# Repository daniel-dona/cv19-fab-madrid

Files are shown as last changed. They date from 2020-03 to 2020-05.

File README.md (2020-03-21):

# cv19-fab-madrid
Existen diferentes modelos que se están imprimiendo, además existen diferentes nomenclaturas para denominarlos. A partir de ahora usaré la nomenclatura contenida aquí: https://publishwith.me/QvTsJTppfb

##¿Qué imprimo?
Primero, antes de nada, imprime el modelo de calibración, deberás hacerlo siempre que cambies de extrusor u otro parámetro importante de tu impresora. Ajusta la expansión horizontal (y si quieres prueba también con el flow rate, pero es opcional). Si el modelo no entra, baja de -0.1 en -0.1 hasta que entre, si queda muy flojo, al revés.

Una vez calibrada, intenta imprimir el modelo acordado, actualmente (21/03/2020) es el HH-1 que puedes encontrar en la carpeta de modelos. También dentro puedes consultar un PDF con recomendaciones para imprimir la máscara.

¡A imprimir!

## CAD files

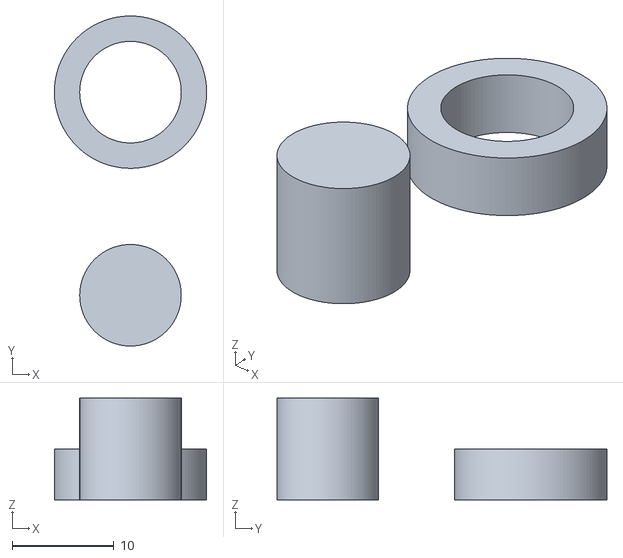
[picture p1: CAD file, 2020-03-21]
calibración/flow_calibrator.stl
15.0 x 32.5 x 10.0

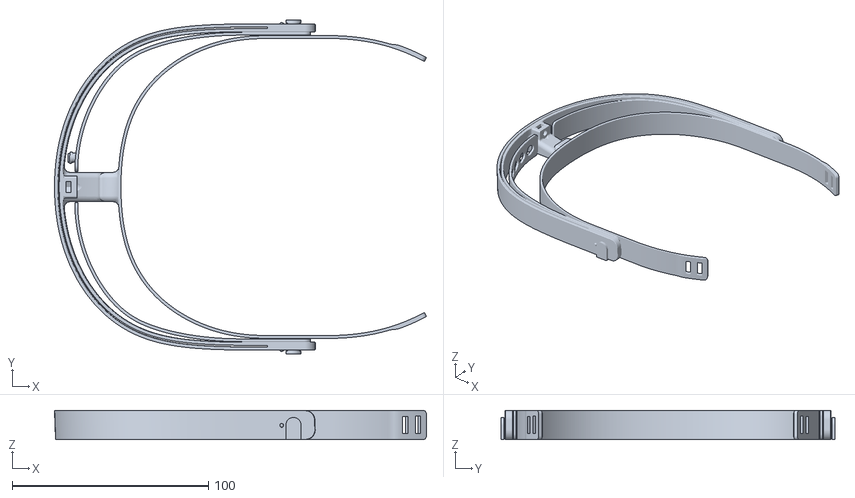
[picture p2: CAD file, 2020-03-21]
modelos/3.5.1/Visera_3.5.1_abierto.stl
189.7 x 170.4 x 15.0

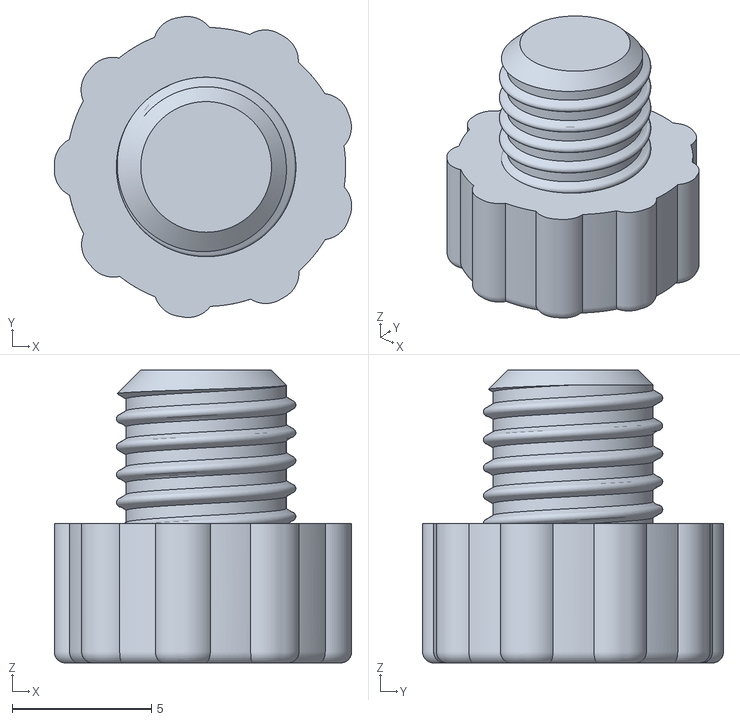
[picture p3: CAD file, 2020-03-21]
modelos/3.5.2/Tornillo_3.5.2.stl
10.7 x 10.8 x 10.5

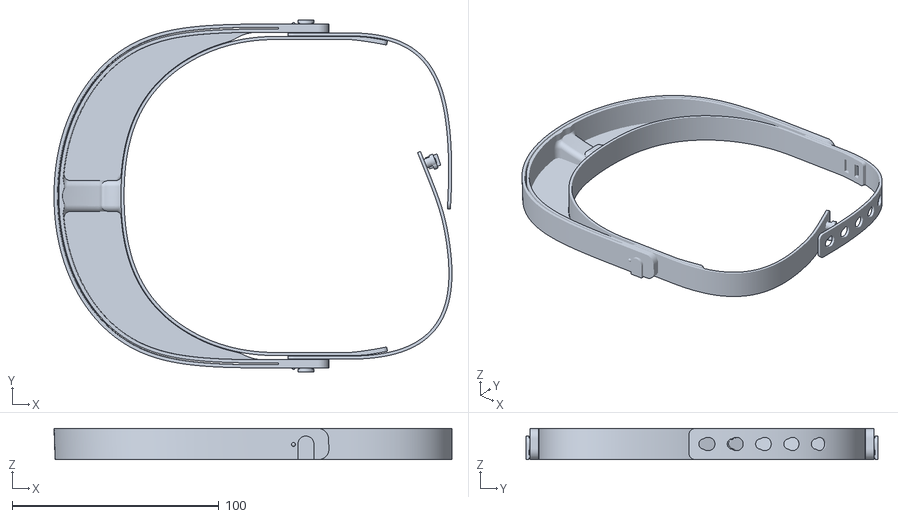
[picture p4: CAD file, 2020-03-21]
modelos/3.6b/Visera_3.6b_cerrada__mas_simple.stl
192.6 x 170.4 x 15.0

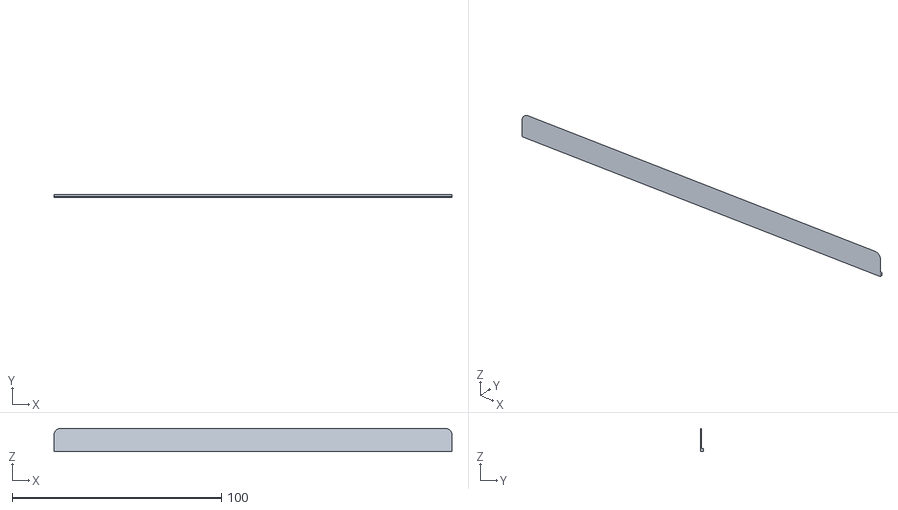
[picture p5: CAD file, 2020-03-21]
modelos/HH-1/Fijador_laminas_finas_300um.stl
190.0 x 1.20 x 11.0

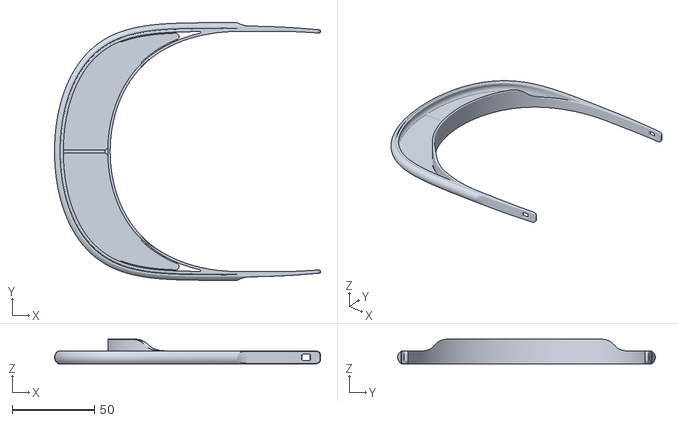
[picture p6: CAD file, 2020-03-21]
modelos/HH-3/Visera_Plana_con_cierre_y_ventilacion_0.3.stl
161.9 x 156.8 x 15.0

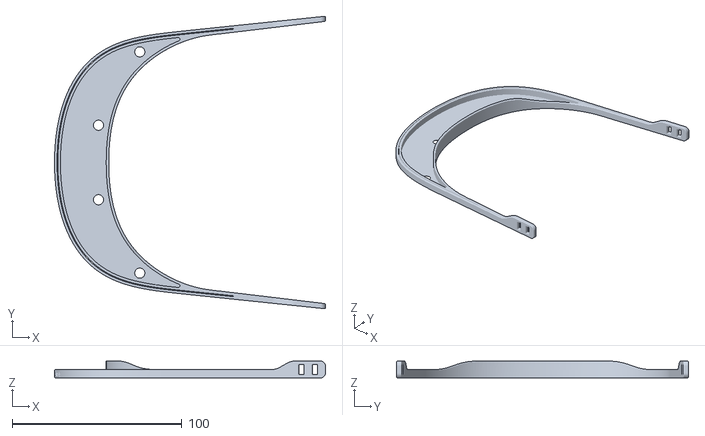
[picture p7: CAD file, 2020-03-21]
modelos/otros/Visera plana con ventilacion.stl
159.8 x 172.4 x 10.0

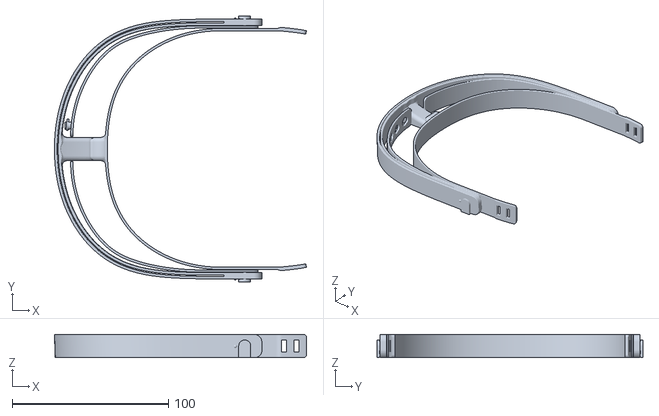
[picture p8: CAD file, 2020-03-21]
modelos/3.5.2/Visera_3.5.2.stl
161.5 x 170.4 x 15.0

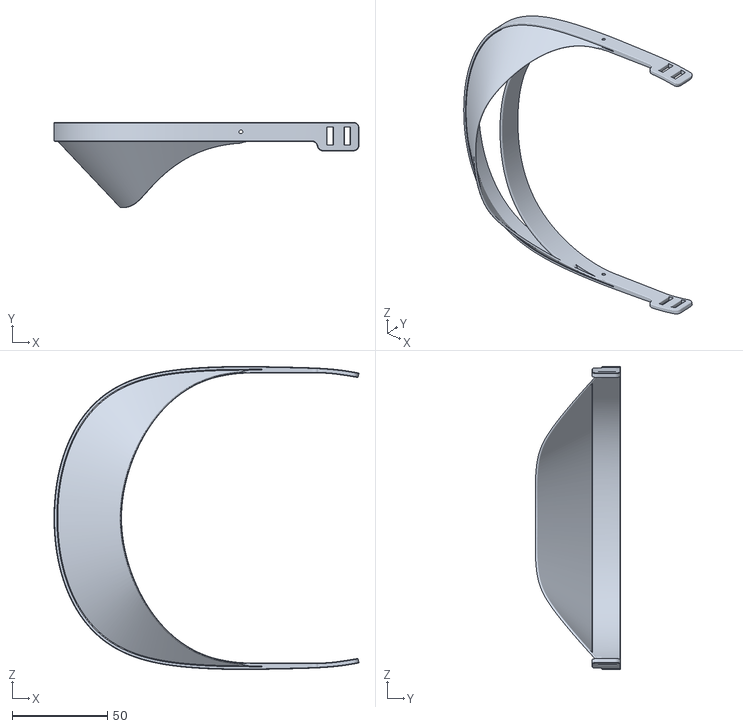
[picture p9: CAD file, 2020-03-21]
modelos/HH-1/Visera_Fija_Cerrada_v0.4_sin_logo.stl
159.9 x 44.8 x 159.0

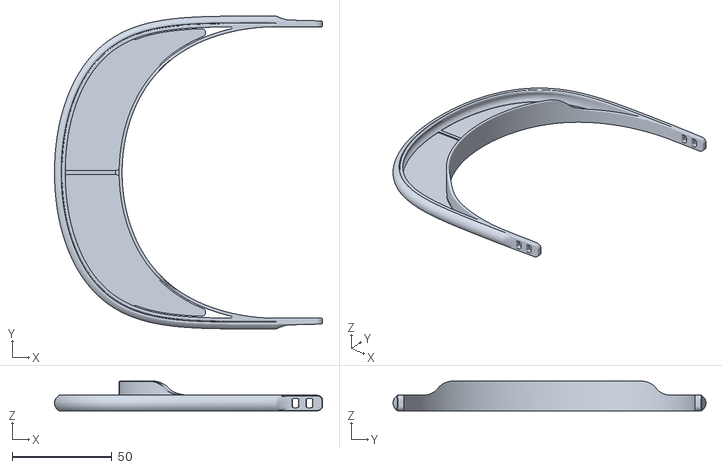
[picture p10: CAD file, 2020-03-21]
modelos/HH-3/Visera_Plana_con_cierre_y_ventilacion_0.4.stl
134.3 x 156.8 x 15.0

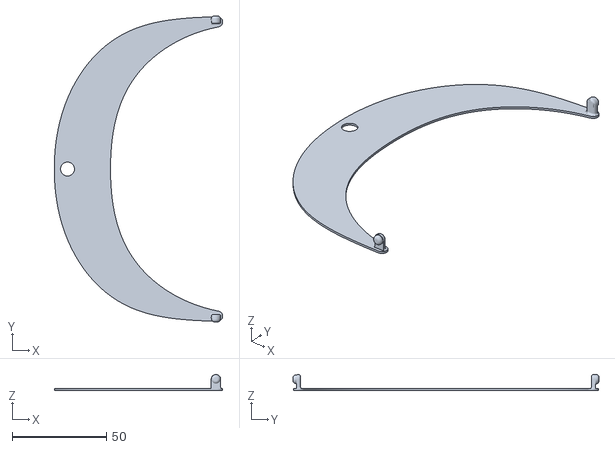
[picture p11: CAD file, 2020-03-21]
modelos/3.5.2/Tapa_3.5.2.stl
89.2 x 162.1 x 8.50

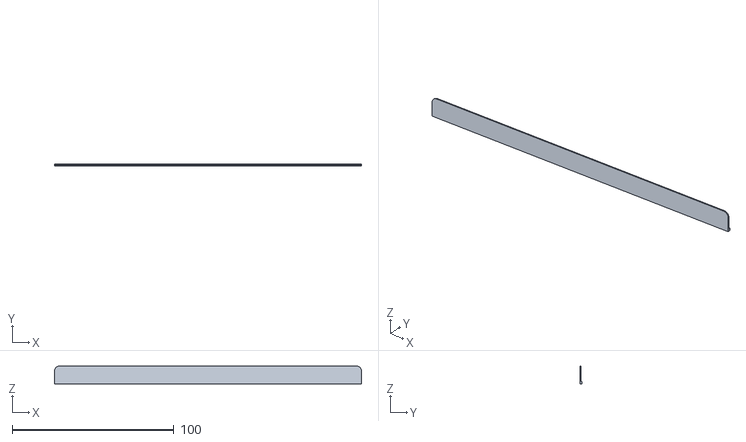
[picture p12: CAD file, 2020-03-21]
modelos/HH-1/Fijador_laminas_finas_600um.stl
190.0 x 1.50 x 11.0

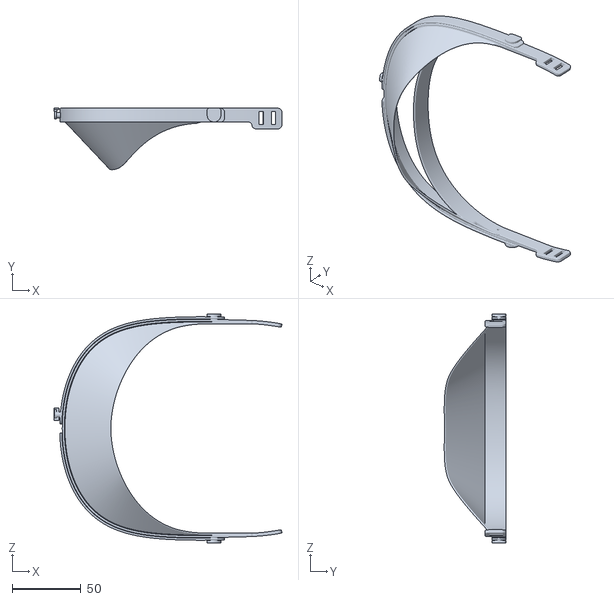
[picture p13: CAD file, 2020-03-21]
modelos/HH-1/Visera_Fija_Cerrada_v0.4_con_cinta_sin_logo.stl
165.9 x 44.8 x 166.3

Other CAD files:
modelos/HH-1/Visera_Fija_Cerrada_V0.4_STEP.step
modelos/HH-1/Visera_Fija_Cerrado_v0.4.stl
modelos/HH-1/Fijador_laminas_finas_500um.stl
modelos/HH-1/Fijador_laminas_finas_400um.stl

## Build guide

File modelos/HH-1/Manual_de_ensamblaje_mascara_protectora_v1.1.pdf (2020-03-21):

# Manual de impresión y ensamblaje mascara protectora

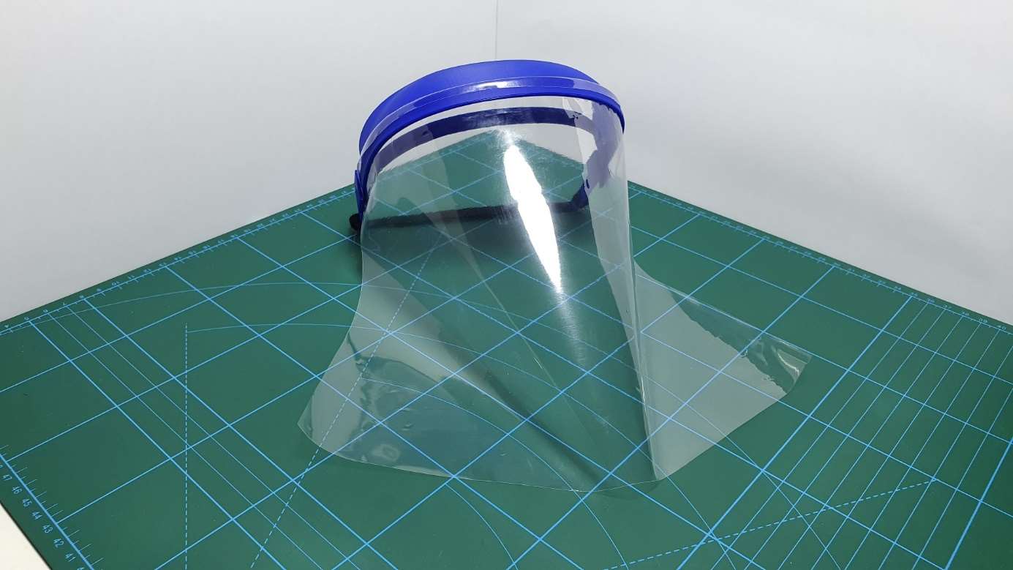
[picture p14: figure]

Página: 2/16

Página: 3/16

# Datos del Documento

Autor: | @YKA3D
Revisor: | @kermithenson
Fecha de publicación: | 18/03/2020
Observaciones:
Para comenzar a fabricar es necesario que la máquina esté correctamente calibrada. Una vez calibrada, se deberá llevar a cabo una prueba de tolerancia.

Test: https://www.thingiverse.com/thing:1662342

# Hoja de Cambios

Fecha | Versión | Autor | Cambios
18 de marzo de 2020 | v.0.1 | @YKA3D | Creación del documento
18 de marzo de 2020 | V.0.2 | @YKA3D | modificación fijación trasera
18 de marzo de 2020 | V.0.3 | @kermithenson | Modificación protocolos
19 de marzo de 2020 | V.0.4 | @YKA3D | Añadir manual modelo simple
19 de marzo de 2020 | V.1.0 | @YKA3D | Documento final
19 de marzo de 2020 | V.1.1 | @YKA3D | Modificaciones varias

# Versión STL

Fecha | Versión | Autor | Cambios
18 de marzo de 2020 | v.3.5 | @Hanochh | Creación STL mascara
18 de marzo de 2020 | V.0.1 | @3DYKA | Creación STL clip

Página: 4/16

# Índice

Introducción | 5
Enlace de compras | 6
Parámetros de impresión | 6
Ensamblaje de la máscara | 8

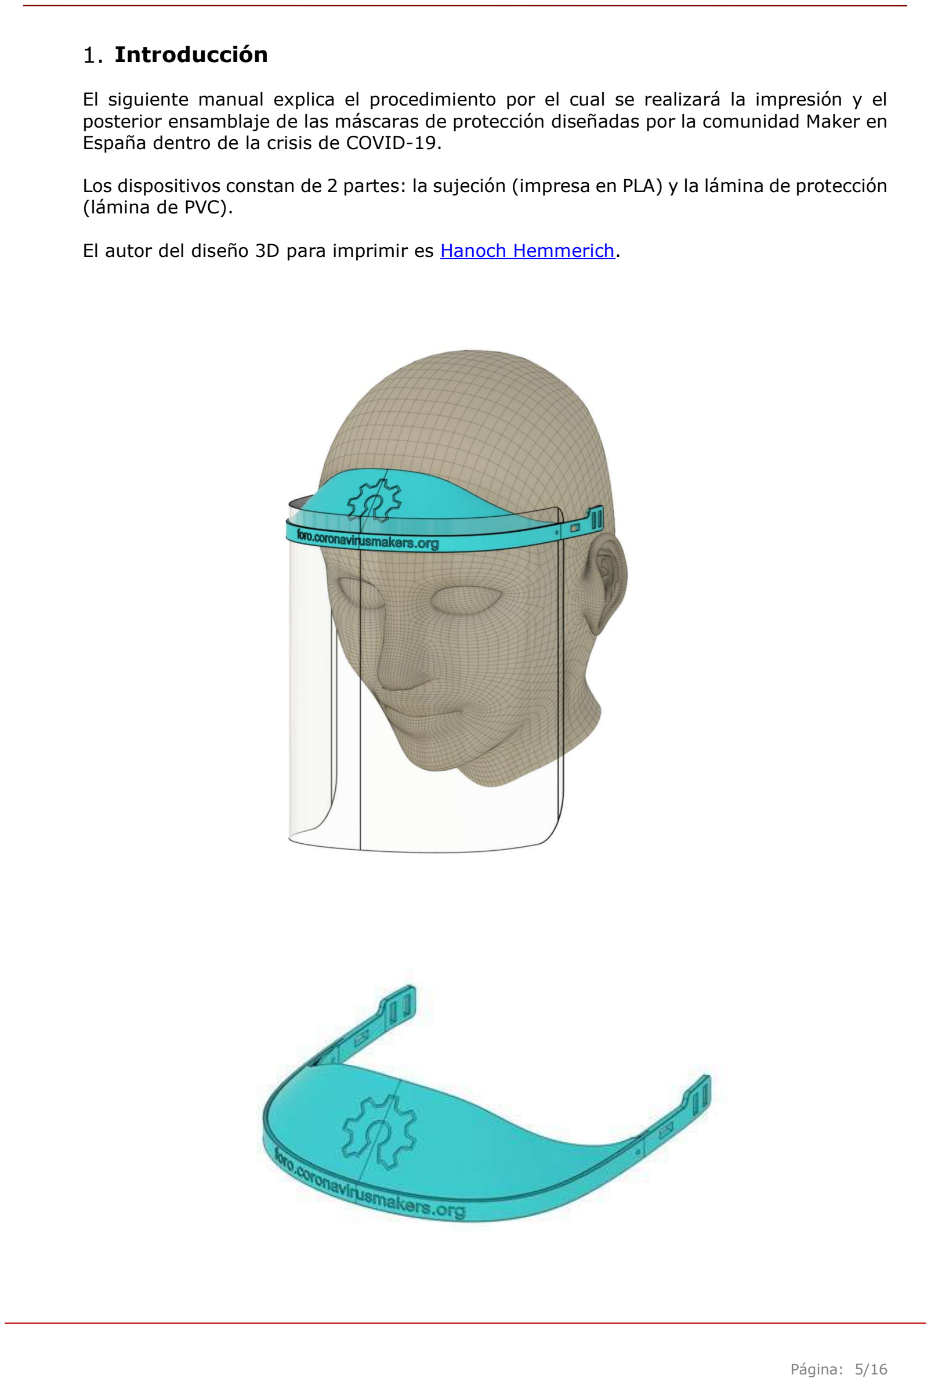
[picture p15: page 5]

Página: 5/16

### Introducción

El siguiente manual explica el procedimiento por el cual se realizará la impresión y el posterior ensamblaje de las máscaras de protección diseñadas por la comunidad Maker en España dentro de la crisis de COVID-19.

Los dispositivos constan de 2 partes: la sujeción (impresa en PLA) y la lámina de protección (lámina de PVC).

El autor del diseño 3D para imprimir es Hanoch Hemmerich.

Página: 6/16

### Enlace de compras

Los siguientes enlaces solo son una referencia del material utilizado para la elaboración de las pantallas protectoras.

- Láminas de encuadernar
o 180 micras
https://www.amazon.es/Fellowes-Cristal-Portadas-encuadernaci%C3%B3ntransparente/dp/B002BARBEK/ref=sr_1_1?__mk_es_ES=%C3%85M%C3%85%C5%BD%C3%95%C3%91&dchild=1&keywords=Fellowes+Portadas+para+encuadernar+de+PVC+transparente+180&qid=1584614023&s=office&sr=1-1
o 240 micras
https://www.amazon.es/gp/product/B000YC1UWG/ref=ppx_yo_dt_b_asin_title_o00_s00?ie=UTF8&psc=1
- Velcro para sujeción trasera https://www.amazon.es/gp/product/B07X2VMHJ5/ref=ppx_yo_dt_b_asin_image_o00_s00?ie=UTF8&psc=1
- Goma elástica
https://www.amazon.es/Banda-el%C3%A1stica-personalizada-Artesan%C3%ADametros/dp/B0749M5CBF/ref=sr_1_16?__mk_es_ES=%C3%85M%C3%85%C5%BD%C3%95%C3%91&crid=2QMWDSOIWQT2U&dchild=1&keywords=bobina+goma+elastica&qid=1584614347&refinements=p_85%3A831314031&rnid=831276031&rps=1&sprefix=bobina+goma+el%2Caps%2C151&sr=8-16

### Parámetros de impresión

El archivo para su impresión se puede descargar desde el siguiente enlace:

### https://www.thingiverse.com/thing:4230817

Los parámetros de impresión utilizados para el modelo son los siguientes:

- Diámetro del Nozzle: 0.4mm
- Altura de capa: 0.28mm
- Relleno: 50%
- Tipo de relleno: Rejilla
- Capas superiores: 4
- Capas inferiores: 2
- Flujo: 80%
- Sin soportes
- Velocidad de impresión:
o Perímetros: 80mm/s
o Perímetros pequeños: 80mm/s o Perímetros externos: 80mms/s o Relleno: 80mms/s
o Relleno solido: 80mms/s
o Relleno solido superior: 80mm/s o Puentes: 80mm/s
o Relleno: 80mm/s
o Recorrido: 180mm/s

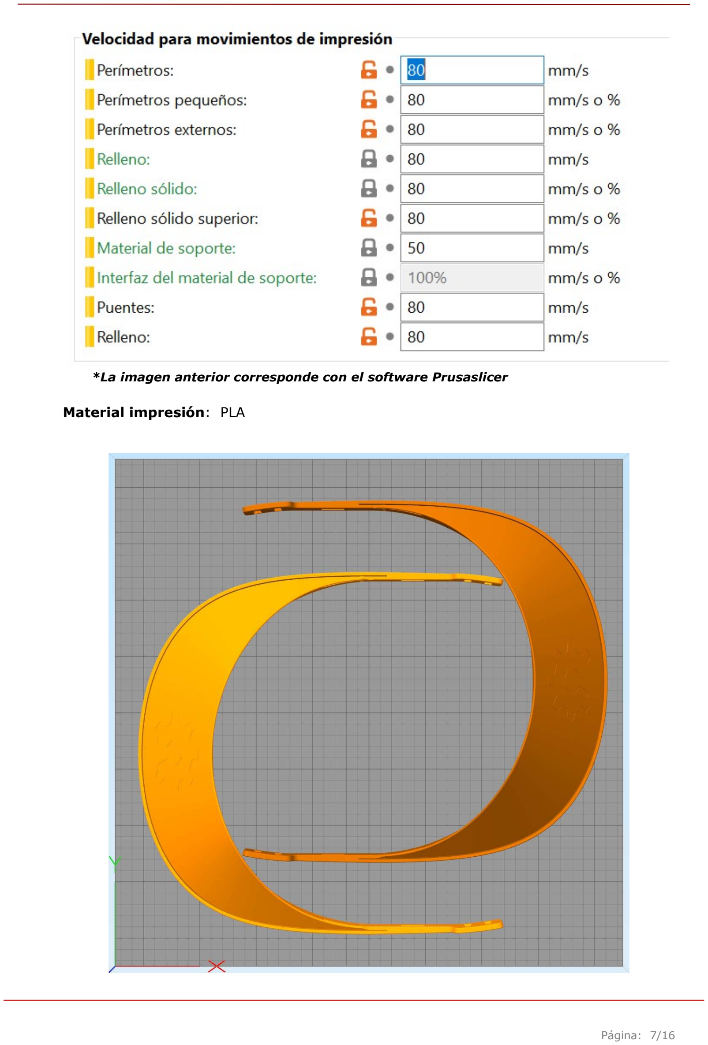
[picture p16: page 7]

Página: 7/16

*La imagen anterior corresponde con el software Prusaslicer

Material impresión: PLA

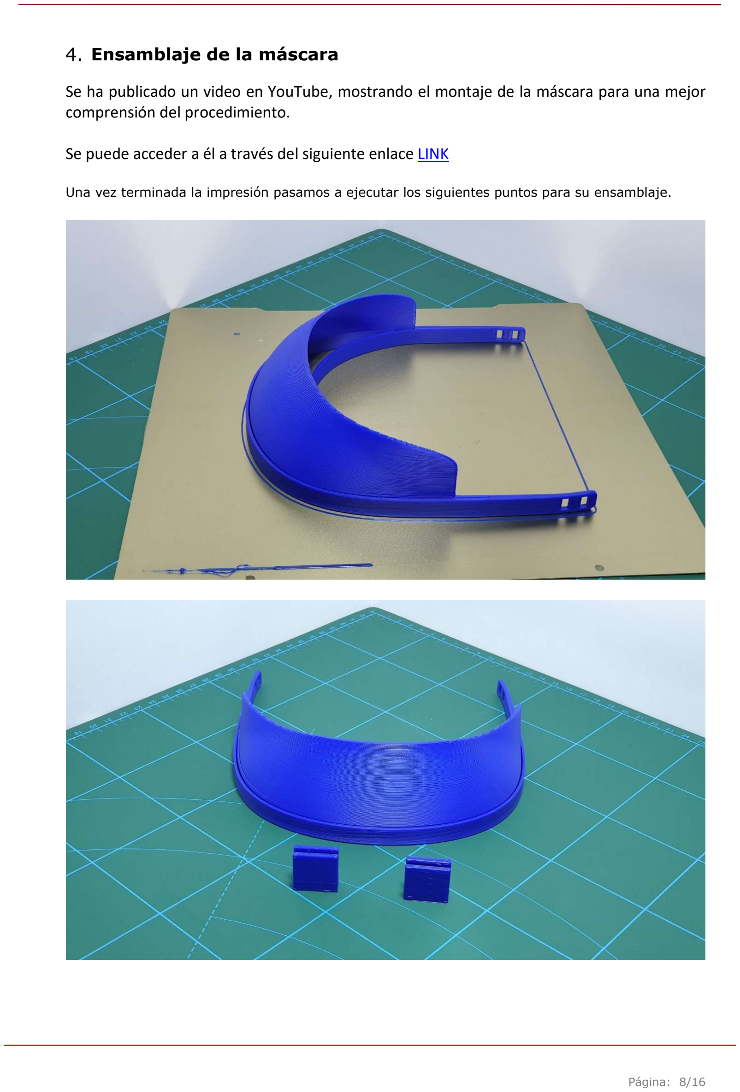
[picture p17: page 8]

Página: 8/16

### Ensamblaje de la máscara

### Se ha publicado un video en YouTube, mostrando el montaje de la máscara para una mejor

comprensión del procedimiento.

### Se puede acceder a él a través del siguiente enlace LINK

Una vez terminada la impresión pasamos a ejecutar los siguientes puntos para su ensamblaje.

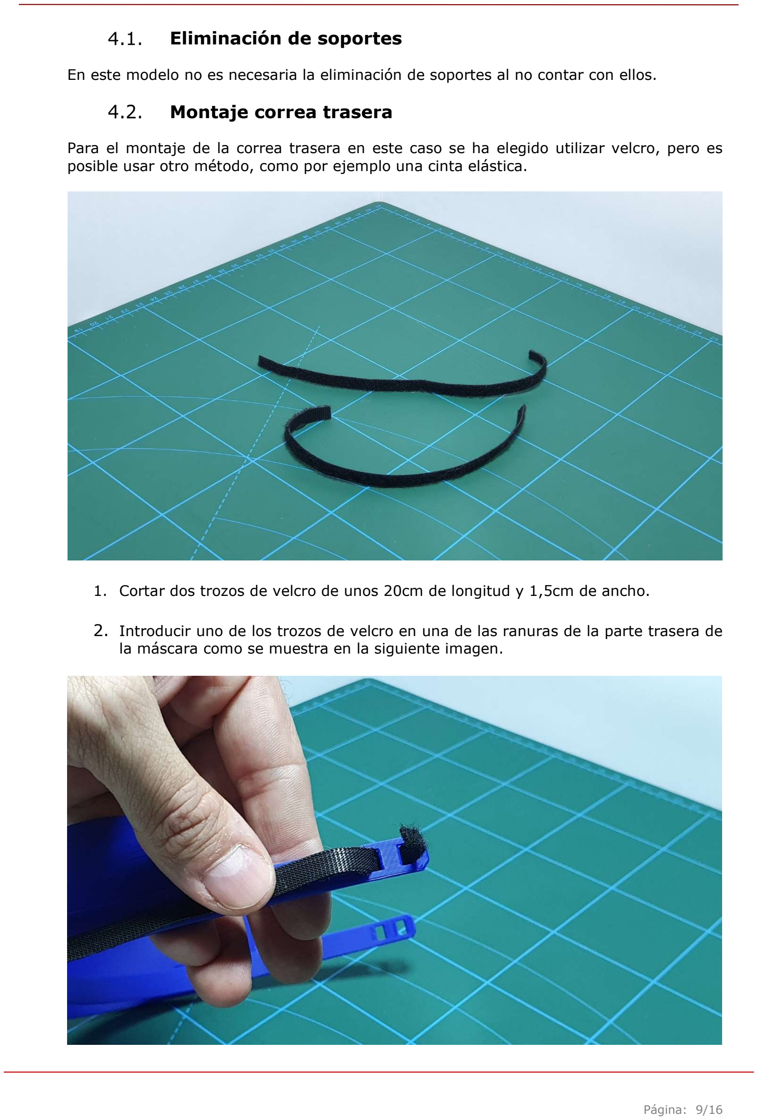
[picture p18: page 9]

Página: 9/16

### Eliminación de soportes

En este modelo no es necesaria la eliminación de soportes al no contar con ellos.

### Montaje correa trasera

Para el montaje de la correa trasera en este caso se ha elegido utilizar velcro, pero es posible usar otro método, como por ejemplo una cinta elástica.

1. Cortar dos trozos de velcro de unos 20cm de longitud y 1,5cm de ancho.

### 2. Introducir uno de los trozos de velcro en una de las ranuras de la parte trasera de

la máscara como se muestra en la siguiente imagen.

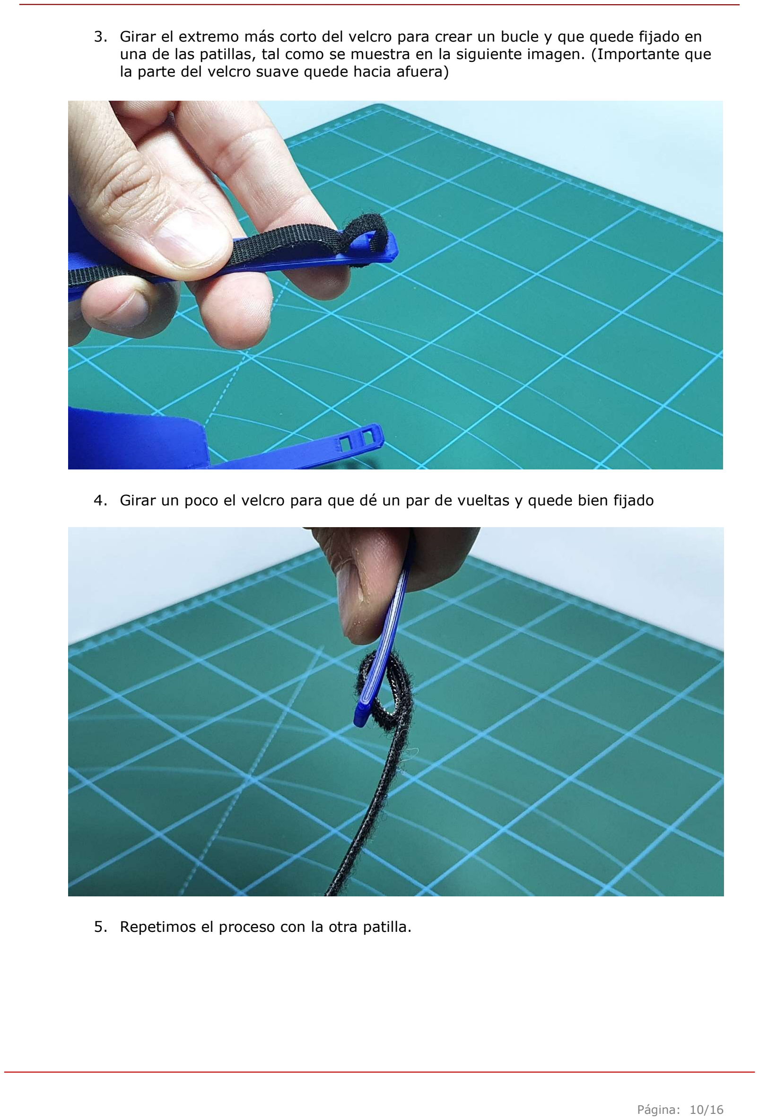
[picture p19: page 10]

Página: 10/16

### 3. Girar el extremo más corto del velcro para crear un bucle y que quede fijado en

una de las patillas, tal como se muestra en la siguiente imagen. (Importante que la parte del velcro suave quede hacia afuera)

### 4. Girar un poco el velcro para que dé un par de vueltas y quede bien fijado

5. Repetimos el proceso con la otra patilla.

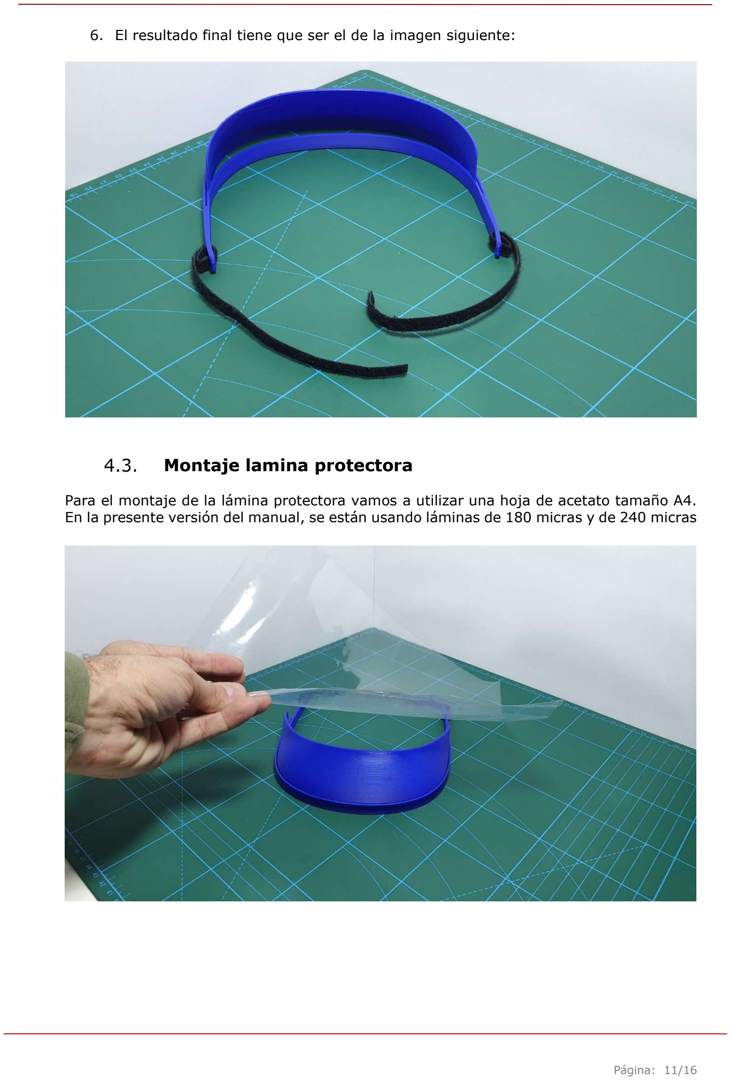
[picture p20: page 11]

Página: 11/16

### 6. El resultado final tiene que ser el de la imagen siguiente:

### Montaje lamina protectora

Para el montaje de la lámina protectora vamos a utilizar una hoja de acetato tamaño A4. En la presente versión del manual, se están usando láminas de 180 micras y de 240 micras

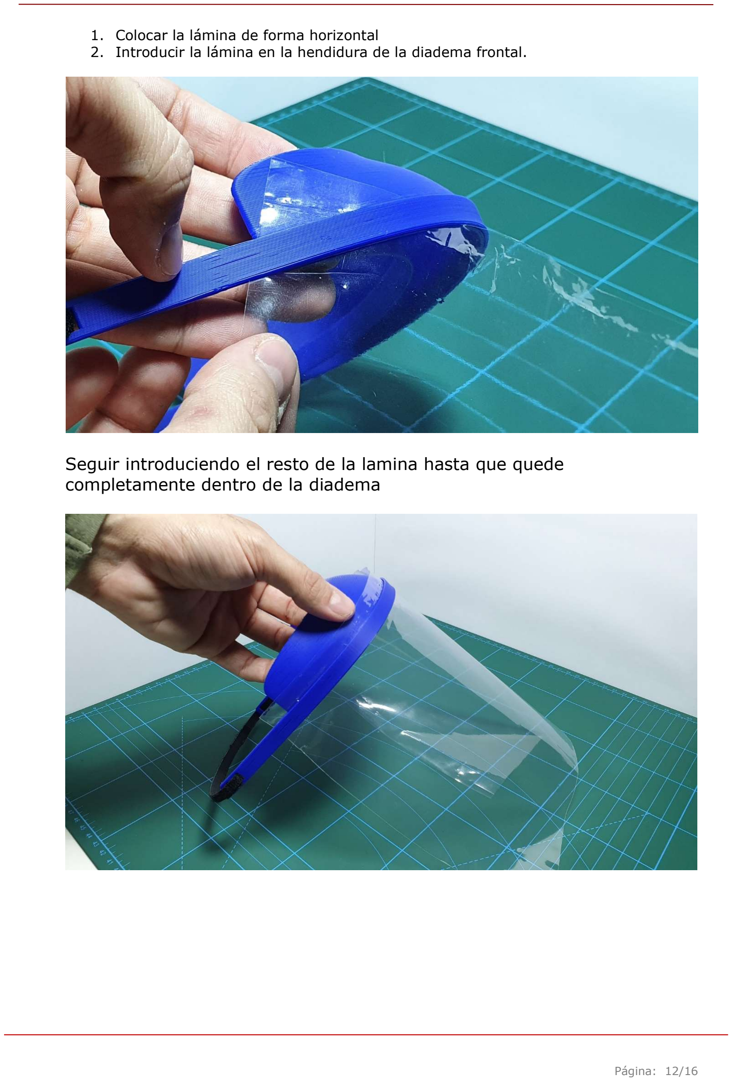
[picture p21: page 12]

Página: 12/16

### 1. Colocar la lámina de forma horizontal

2. Introducir la lámina en la hendidura de la diadema frontal.

### Seguir introduciendo el resto de la lamina hasta que quede completamente dentro de la diadema

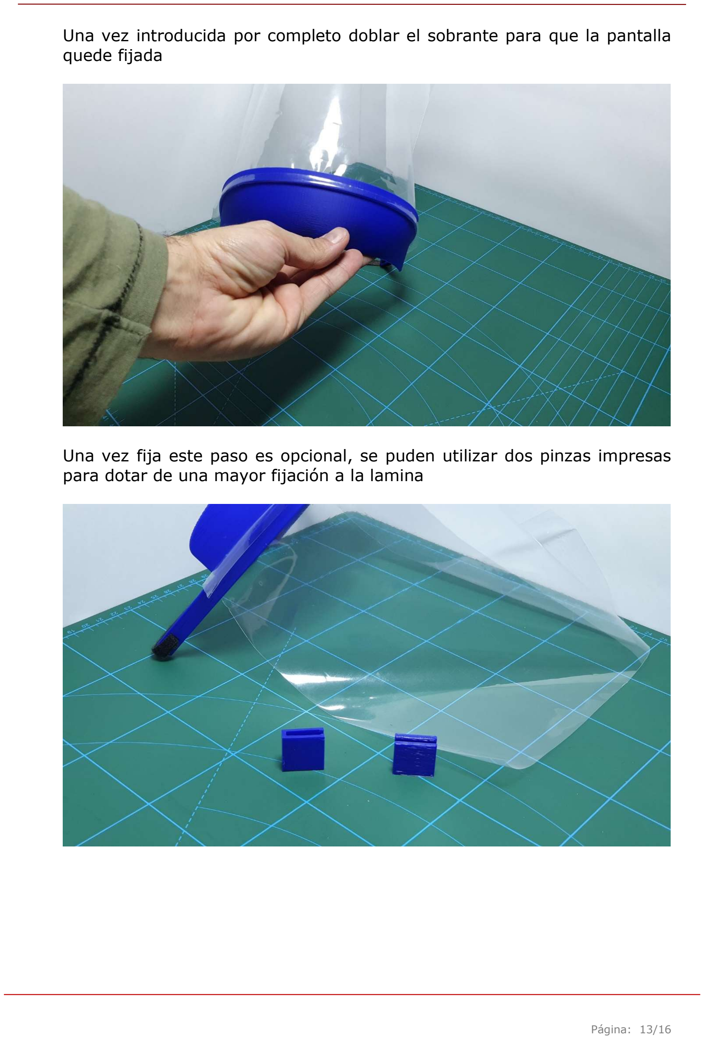
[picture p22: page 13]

Página: 13/16

### Una vez introducida por completo doblar el sobrante para que la pantalla quede fijada

### Una vez fija este paso es opcional, se puden utilizar dos pinzas impresas para dotar de una mayor fijación a la lamina

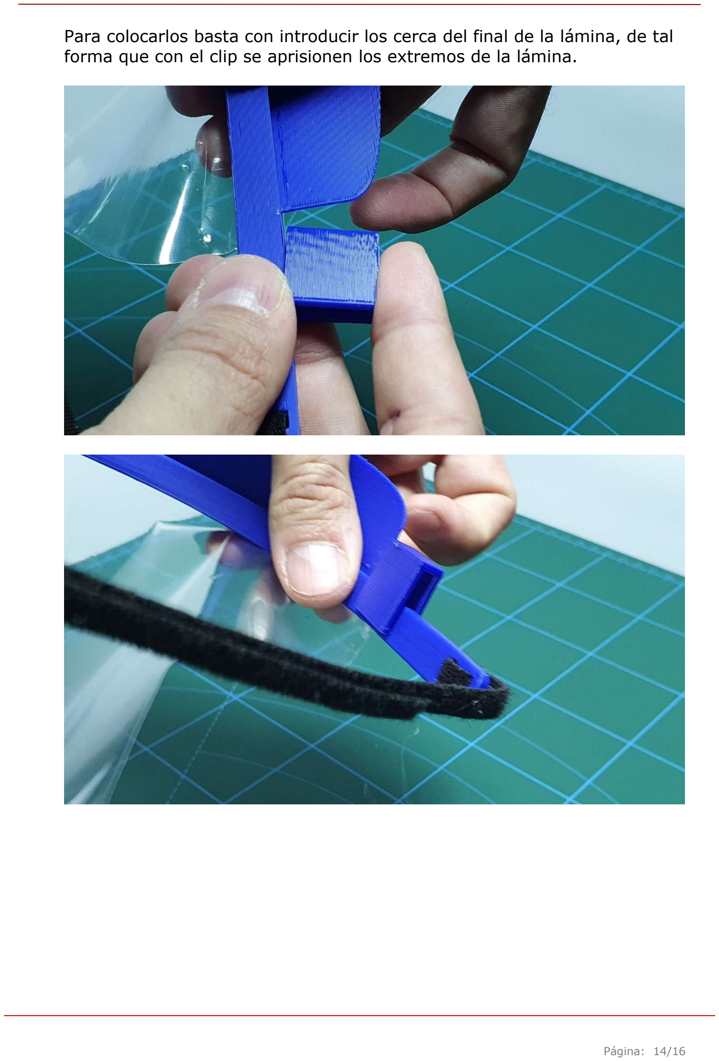
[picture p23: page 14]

Página: 14/16

### Para colocarlos basta con introducir los cerca del final de la lámina, de tal

forma que con el clip se aprisionen los extremos de la lámina.

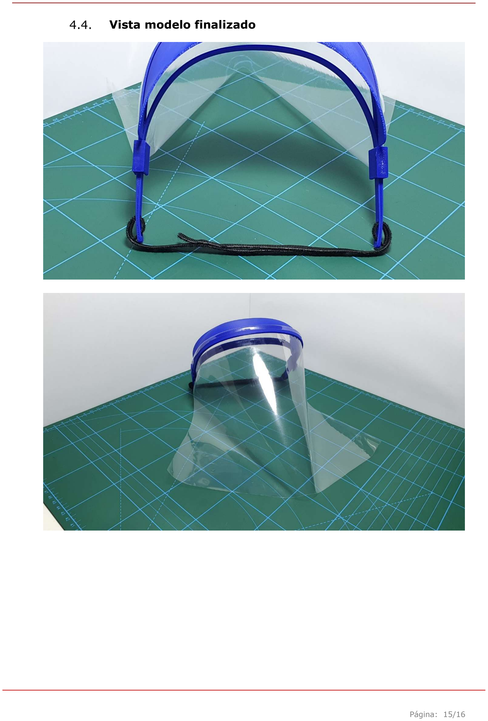
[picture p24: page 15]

Página: 15/16

### Vista modelo finalizado

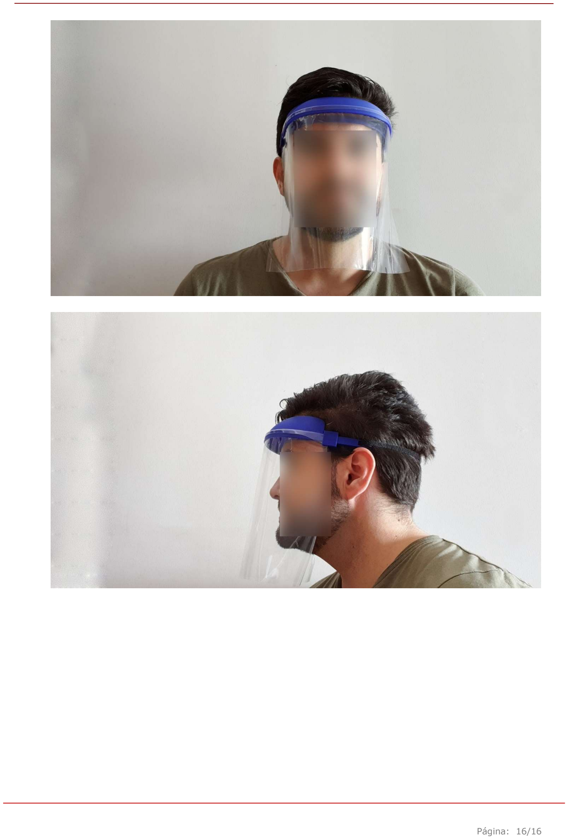
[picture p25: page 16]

Página: 16/16

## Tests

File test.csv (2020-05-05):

Hola | esto | es | una | prueba
para | ver | si | se | puede

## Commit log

2020-03-21 Add STL
    [Visera_3.6b_cerrada__mas_simple.stl, flow_calibrator.stl]
2020-03-21 Más modelos
    [Fijador_laminas_finas_300um.stl, Fijador_laminas_finas_400um.stl, Fijador_laminas_finas_500um.stl, Fijador_laminas_finas_600um.stl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]
